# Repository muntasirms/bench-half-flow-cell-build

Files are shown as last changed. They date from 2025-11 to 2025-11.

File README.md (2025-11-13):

# Bench-Scale Electrochemical Flow Cell Build
Build your own flow cell, for use in standardized flow battery and slurry electrode experimental systems. Can use electrolyte chamber for half cell measurements or two of the same for full cell measurements. 

**NOTE: This is precariously maintained/documented and very much a work in progress. Please feel free to reach out to me at mshahabuddin [at] wpi [dot] edu for any questions if attempting to build before fully documented.**



## Bill of Materials 
### In this repo:
- 1 "Inlet" type plate fabricated per "half cell" tested (i.e. for half cell measurements, only 1 inlet plate required)
- 1 "Cell Channel" type plate fabricated per "half cell" tested. Can adjust cell thickness to resolution of your print.
- 1 "Non conductive plate" type plate fabricated per "half cell tested", unless machining current collector directly
- For half cell measurements, 1 electrolyte chamber
### To purchase
- Separator material (chemistry specific - I typically use a size exclusion/non-ion selective separator. For example a [polypropylene size exclusion separator](https://celgard.shop/collections/all)
- Gasket sheet (I use [silicone](https://www.mcmaster.com/8525T41/). Will need to cut 
- [M4 threaded rods](https://www.mcmaster.com/94185A145/) (or bolts if preferred). Nonconductive material if using graphite plate or metal plate current collector.
- [M4 nuts](https://www.mcmaster.com/94150A335/), I typically use flange nuts but their diameter may be too large for some of the inlet channels.
- IDEX fittings and associated tubing
- 1/8" EPDM O-ring (or material of choice)
- Graphite foil or graphite plate if machining current collector
- Glue (superglue works well, conductive glue would be better)
### Tools
- Hand drill or drill press
- Bench vice
- 1/4"-28 Bottom Tap

## (Non-comprehensive) Instructions
1. Print parts as per the bill of materials.
    - Note filament materials - make sure your printed materials resist your chosen electrolyte materials. In general, PP is resistant to most aqueous electrolytes across a broad range of pHs, but is much more mercurial to print. PLA works fine for most acidic/mild pH electrolytes but will hydrolyze in concentrated base. 
2. Into each printed inlet plate, use the bottom tap to create threading for IDEX fittings
3. Place 1/8" O-rings into threaded holes
    - sometimes the threads will leak even with the IDEX ferrules due to print lines not sitting flush with the ferrule. The O-rings seem to consistently fix this issue even relatively high flowrates/pressure.
4. (for half cell) Cut gasket sheeting for electrolyte chamber
    - can use a vectorized version of the cell channel model to cut using a cutting tool like a Cricut. I usually just use a printed cell channel part and use it as a stencil to cut the flow channel shape out of the gasket sheet. For holes, a typical hole punch works and accommodates M4 bolts well.
5. Cut gasket sheeting for current collector backing
    - Cut outline of "cell channel", but rather than the cutting the full cell channel, cut holes by the inlet and outlet ports of the inlet plate. This will result in a gasket of the same dimensions as the cell channel, but with 8 holes - 6 for each bolt, 2 for the inlet and outlet of the flow channel
5. Cut strip of separator material such that it covers the entire with of the cell channel but fits within the total width between two of the bolts.
6. Taking non-conductive plate print, glue graphite foil to cover at least the portion of the non-conductive plate exposed to the cell channel and at least enough overhang to clip electrical connection to -- this is where your test equipment will connect to your working electrode
7. Sandwich together all components:
    - Half cell will have the following order: "inlet" plate - current collector gasket - "non-conductive" plate - (adhered to) graphite foil - cell channel -> separator sheet -> electrolyte chamber gasket -> electrolyte chamber
    - Full cell will have the following order: "inlet" plate -> current collector gasket -> "non-conductive" plate -> (adhered to) graphite foil -> cell channel -> separator sheet -> cell channel -> graphite foil -> (adhered to) "non-conductive" plate -> current collector gasket -> "inlet" plate
        - Full cell has not been properly leak tested - consider printing the cell channels out of compressible polymers (Shore ~60-70) for better hermetic contact between cell channels. In the worst case (worst because it offers less control over channel thickness), consider using electrolyte chamber gaskets on either side of the separator.
    - The bolts should fit easily through each layer. Nuts will screw on either end and can be tightened to desired torque
8. If that somehow made sense - congratulations! You should have a testable flow cell.

Here is an example image. Note that this is from earlier versions of this project so the geometries of each part may not align with the models. **TODO: include more instructive images/figures for each step.**



## Build/compatibility notes
- The cell electrolyte chamber has ~10 mm hole diameters on the top, built to accomodate 9.5 mm OD reference electrodes like from [Pine Research](https://pineresearch.com/products/reference-ag-agcl-standard-single/)
- Note that the gaskets are _outside_ the current collector and separator - the only part that defines the thickness of the channel is the thickness of the cell channel spacer. This allows granular tuning of channel thickness by printing channels of varying thickness
    - This was intentionally done to more easily study electrode thickness which slurry electrodes are sensitive to. This also means channel thickness won't change with compression/torque.
- There is a third small hole in the electrolyte chamber - it was originally intended for gas sparging but may also be used for electrolyte recirculation in the electrolyte chamber. In the current version bubbles may occlude the reference/counter electrodes which can result in some noise. I included small holes at the top of the reference electrode port to allow for slightly better gas distribution. Your mileage may vary.
- Inside each "part type" folder, there may be multiple versions of a "part type". For example for "inlet" parts, there is a closed flow manifold if only the flowing electrolyte is of interest. If, for example, an electrode is under study, there is an additional "air electrode" inlet plate that includes an `8 mm x 20 mm` window open to the air, where the current collector can be replaced by an air electrode membrane electrode assembly.
- The flow channels have exposed surface areas of about `232 mm^2`. After accounting for the inlet port holes, the current collector surface area is `207 mm^2`. This will generally vary slightly with printer tolerance but most decent printers will get it within the square mm.To clarify:



# Fine Print

## License Summary
CC BY-NC-SA 4.0
- **Attribution (BY)**: Please give appropriate credit.
- **Non-Commercial (NC)**: Usage is limited to research, educational, and personal applications.
- **Share-Alike (SA)**: Any derivatives must be shared under the same license.

## Allowed Uses
- Personal projects
- Educational or research purposes
- Non-commercial open-source projects
- Modifying and sharing designs under the same license

## Disallowed Uses
- Selling the files or any product derived from them
- Using the designs in a commercial project without explicit permission
- Removing attribution or license information

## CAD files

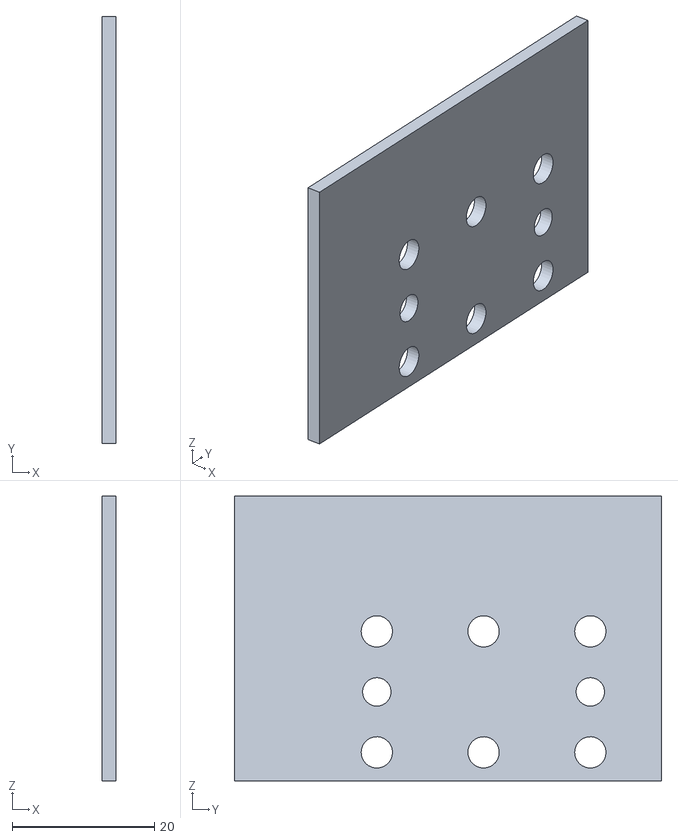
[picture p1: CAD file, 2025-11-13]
currentCollectors/nonConductiveCurrentCollectorSupport.stl
2.00 x 60.0 x 40.0

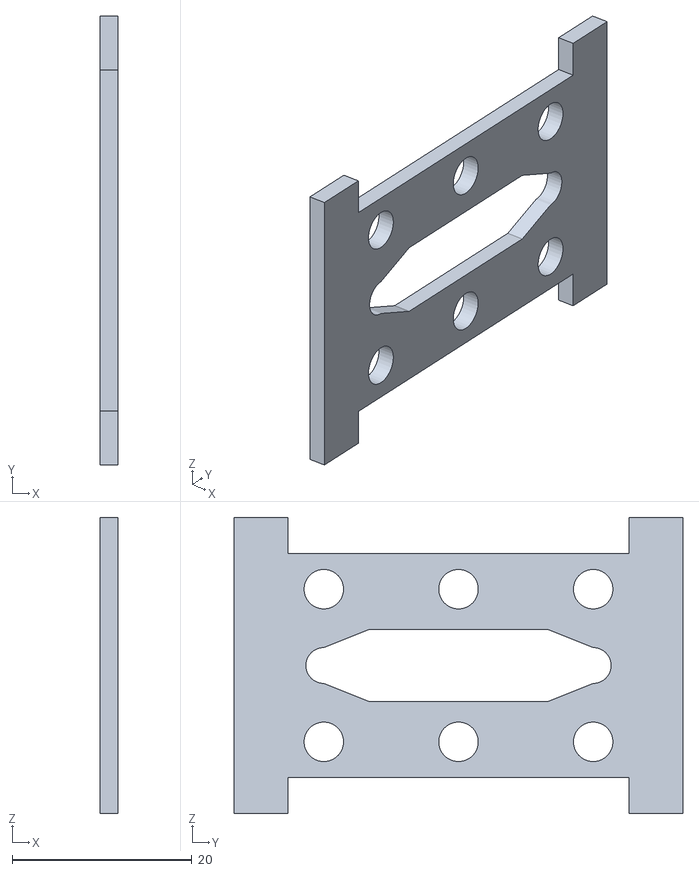
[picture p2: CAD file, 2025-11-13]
flowChannels/modChannelwTabs.stl
2.00 x 50.0 x 33.0

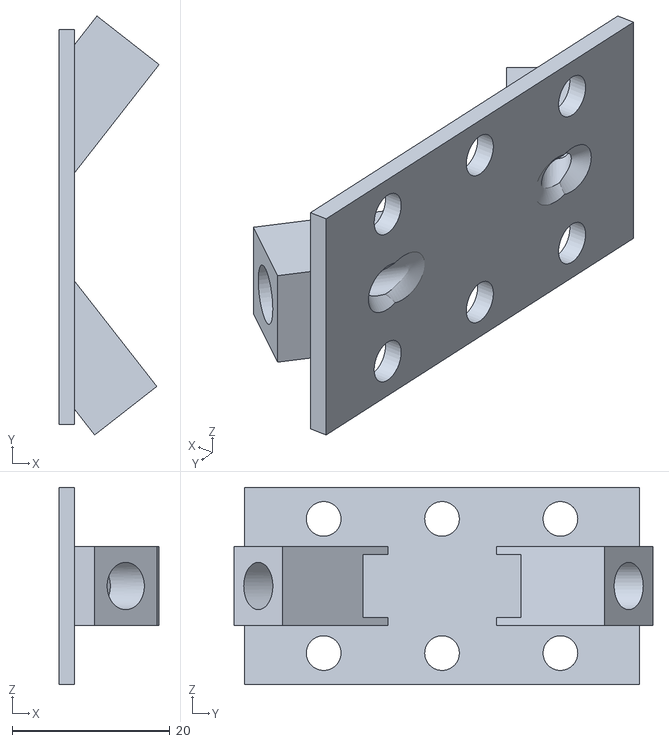
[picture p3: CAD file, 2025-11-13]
flowInlets/modularFlowCellDiagonalInletv3.stl
12.7 x 53.1 x 25.0

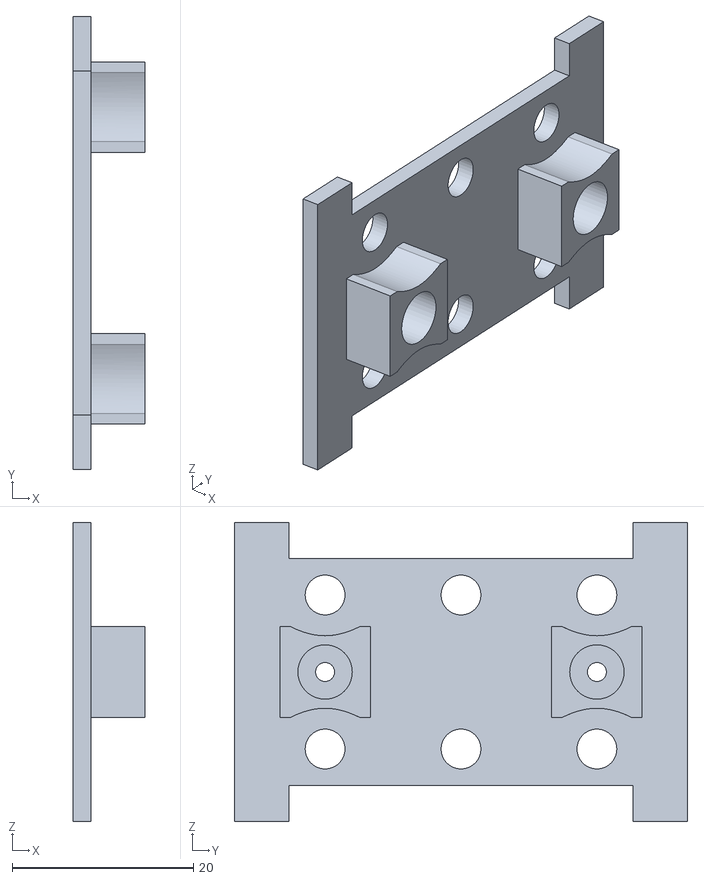
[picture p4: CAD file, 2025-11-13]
nonConductiveCurrentCollectorSupport.stl
8.00 x 50.0 x 33.0

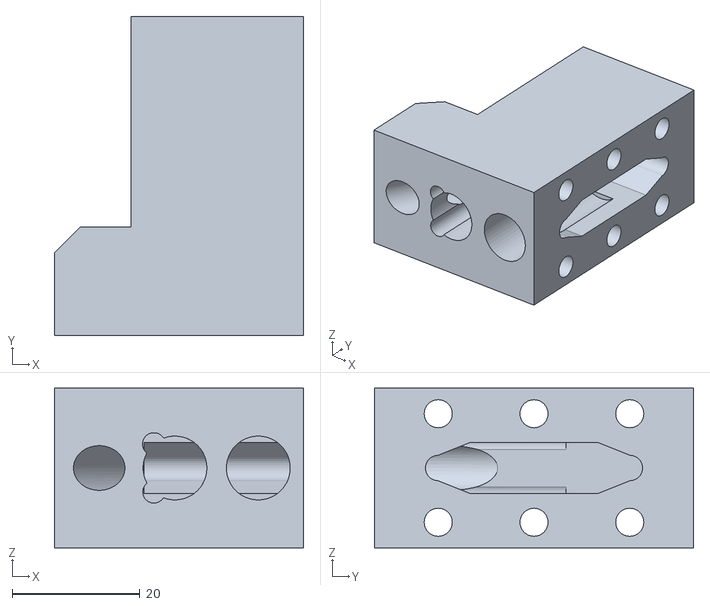
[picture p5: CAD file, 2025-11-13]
electrolyteChamberLargeThroughHole.stl
39.0 x 50.0 x 25.0

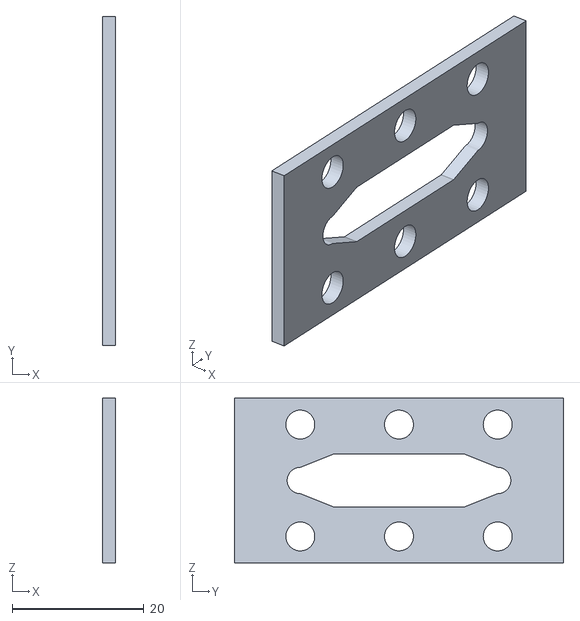
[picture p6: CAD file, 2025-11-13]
flowChannels/modularCellChannel.stl
2.00 x 50.0 x 25.0

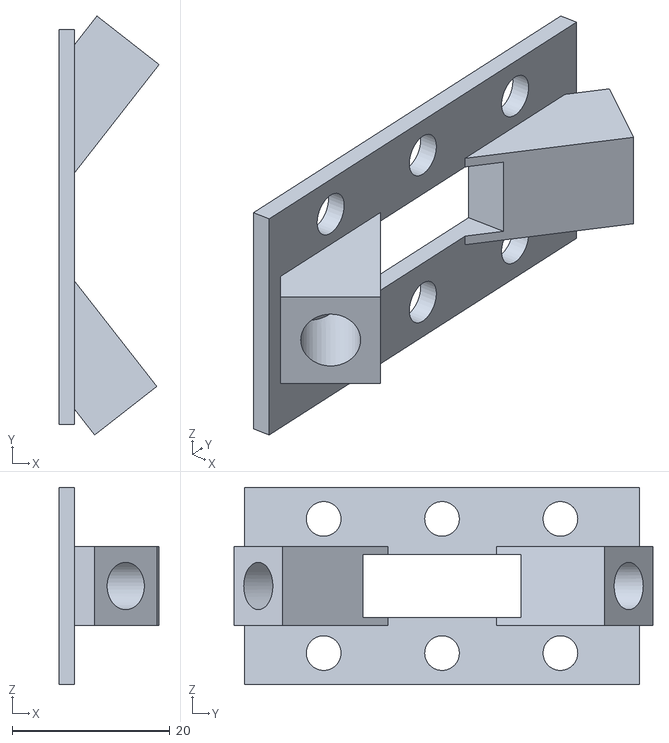
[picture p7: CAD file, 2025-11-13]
modFlowCellAirElectrodeInlet.stl
12.7 x 53.1 x 25.0

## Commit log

2025-11-13 Added flow cell channel parts
    Added flow cell channel parts - need to include naming guide on each
    [electrolyteChamberLargeThroughHole.stl, modChannelwTabs.stl, modFlowCellAirElectrodeInlet.stl, modularCellChannel.stl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]
2025-11-13 Enhance README with part type and flow channel info
    Added details about part types and flow channel dimensions.
